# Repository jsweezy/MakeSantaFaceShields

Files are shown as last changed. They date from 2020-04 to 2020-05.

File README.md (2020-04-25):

# MakeSantaFaceShields
Face shield project for MakeSantaFe for COVID-19 aid for Santa Fe, NM.  

## Summary
Slight modification of the 3DVerkstan face shield frame to support stacking with PETG.

## Details
This was developed for stacking with PETG on a Prusa i3 Mk3. The original 3DVerkstan design is imported into 
OpenSCAD. A custom interface layer of 0.3mm is added between frames.  The interface layer consists of small 
cylinders along the arms of the frame.  Over the drip tray a bridge is added to support the next frame. The print 
settings for this layer are modified in Prusa Slicer. The nozzle temperature is lowered to 215C from the standard 250C, 
the fan is turned to 100%, and the print speed is slowed significantly.  This causes a delamination layer where the 
interface layer will fail to adhere to the frame below it. The interface layer will adhere to the frame above. 

There are two Perl scripts provided that generate custom GCODE and layer information for Prusa Slicer. These
are in the `Scripts` directory and include:\
`generate_gcode_for_PrusaSlicer.pl` - Generates custom GCODE\
`generate_layer_config_ranges_for_PrusaSlicer.pl` - Generates custom layer ranges

These scripts are used to modify Prusa project files, which are contained in a zip format.  If the print temperatures
need to modified then the Scripts need to be modified, the temperatures are set with a variable. The nozzle and bed temperatures need to also be set in Prusa Slicer. The procedure for modifying a project file is:

1) Make a directory for the project files and change to that director:\
`mkdir test_project`\
`cd test_project`
 
2) Unzip the Prusa project file.\
`unzip ../PrusaProjectFiles/8stack_test_petg.3mf`

3) Apply the custom GCODE generating script:\
`../Scripts/generate_gcode_for_PrusaSlicer.pl > Metadata/Prusa_Slicer_custom_gcode_per_print_z.xml`

4) Apply the layer config ranges script:\
`../Scripts/generate_layer_config_ranges_for_PrusaSlicer.pl > Metadata/Prusa_Slicer_layer_config_ranges.xml`

5) Recombine the files into a single Prusa project file:\
`zip ../PrusaProjectFiles/new_project.3mf -r *`

Now the new project file can be opened in Prusa Slicer and sliced. 

## Variations from the standard 3DVerkstan design

The goals was to make as few modifications to the 3DVerkstan design as possible. Such as maintaining the sweat drip tray. 
Some modifications for stacking fill in the drip tray. But the drip tray seems like an important design feature.  

### Drip Tray

The drip tray is slightly thickened to prevent damage when seperating the frames.  The original design was only 2 layers
thick for a 0.3mm layer height.  This also seemed to allow small holes if slight imperfections are made during a layer.  The
drip has been thickened to be 4 layers thick for strength and to prevent small holes. 

The interface layer contains a bridge below the drip tray.  The bridge will generally adhere well to the drip tray and provide another layer.  

### Arms

Small cylinders to seperate and support the frames have been added.  The design has been modified from IQLess (see reference below).  These cylinders can be easily removed but are not generally significant.   

### 

## References

### National Institues of Health page for this design:
https://3dprint.nih.gov/discover/3dpx-013306

### 3DVerkstan Page:
https://3dverkstan.se/protective-visor/

### Matterhackers Page for 3DVerkstan Design:
https://www.matterhackers.com/store/l/protective-face-shield/sk/M7LP9Q7M

### IQLess YouTube Channel
OpenSCAD support idea from: https://www.youtube.com/watch?v=apcrs6d_irc\
"Covid: Stacking Prusa RC3 and 3Dverkstan face shields Using Openscad"\
By iqless. OpenSCAD here is a modification of his file which can be found at:\
https://gist.github.com/patmandenver/847a0bf508b523487a3708c39c799950

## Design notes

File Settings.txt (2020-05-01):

Settings by material / manufacturer

* PETG

  - Overture
    * Diameter 1.27 
    * Bed Temp - 85/90 
    * Nozzle - 250C

  - Keene Village Plastics
    * Stacking has been well tested on Prusa Mk3
    * Diameter 1.25
    * Bed Temp - 85/90 -  May need to increase to prevent delamination during printing when fan to turned to 100%
    * Nozzle Standard - 250
    * Nozzle Interface - 215
    * Nozzle First Layer - 230
    * Fan Interface - 100%
    * Speed Interface - 3 mm/sec for perimeters, 6 mm/sec for infill

* PLA 

  - Overture
    * Diameter - 1.28 mm
    * Bed Temp - 60C
    * Nozzle Standard - 215C
    * Nozzle Interface - 180C
    * Nozzle First Layer - 195C
    * Notes:  Empty interface of 0.2 mm height with interface layer of 0.2 mm height

  - HatchBox
   
  - Matterhackers

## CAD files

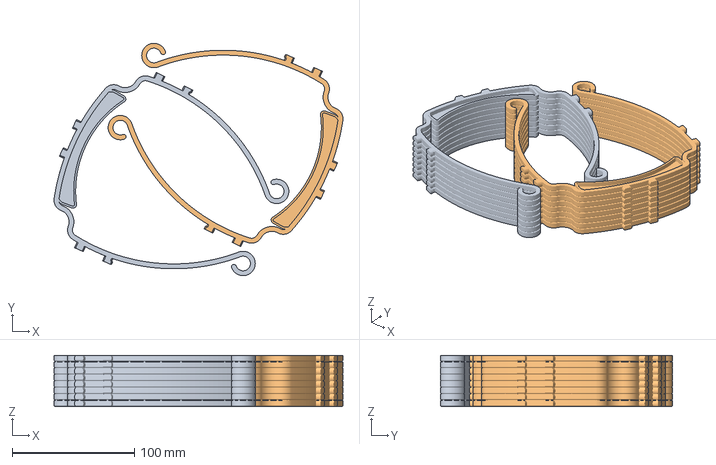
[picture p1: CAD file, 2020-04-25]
PrusaProjectFiles/PETG/2x8stack_petg.3mf
236.9 x 190.4 x 42.1 mm
3DVerkstan_6_hole_AMERICA_v3 x 20 (0.2mm gap) (1).STL x 2

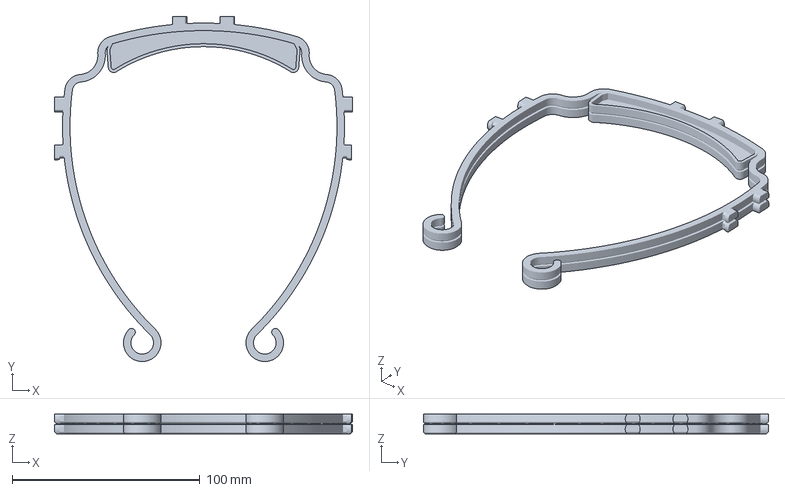
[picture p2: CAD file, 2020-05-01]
PrusaProjectFiles/PLA/2stack_pla_overture.3mf
158.5 x 183.6 x 10.4 mm

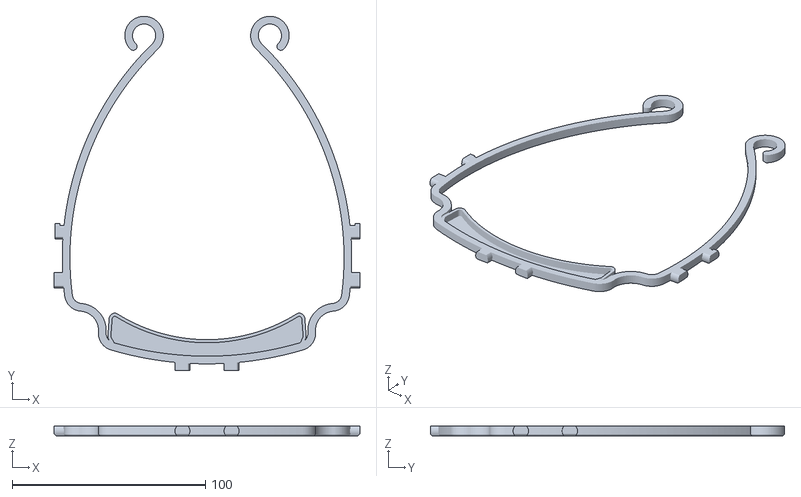
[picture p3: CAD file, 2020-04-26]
STLs/modified_frame.stl
158.5 x 183.6 x 5.00

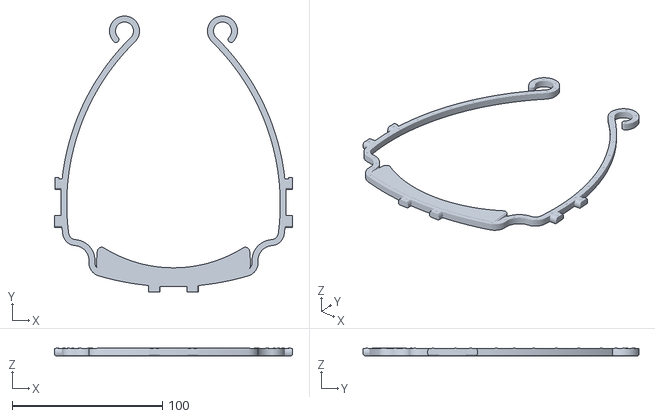
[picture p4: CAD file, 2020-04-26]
STLs/PETG/single_stackable_lower.stl
158.5 x 183.6 x 5.30

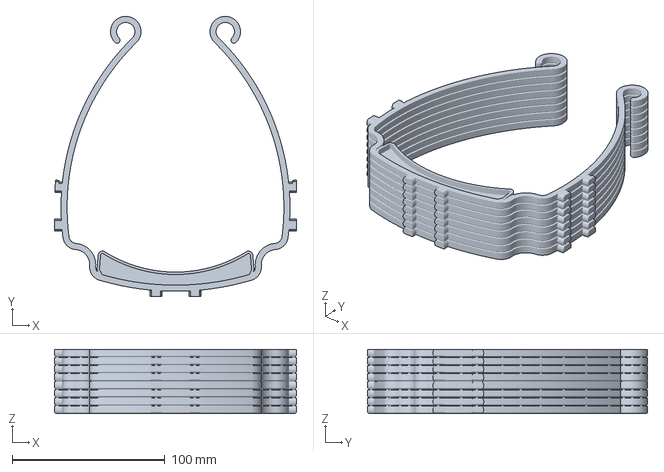
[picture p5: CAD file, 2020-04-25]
PrusaProjectFiles/PETG/8stack_test_petg.3mf
158.5 x 183.6 x 42.1 mm

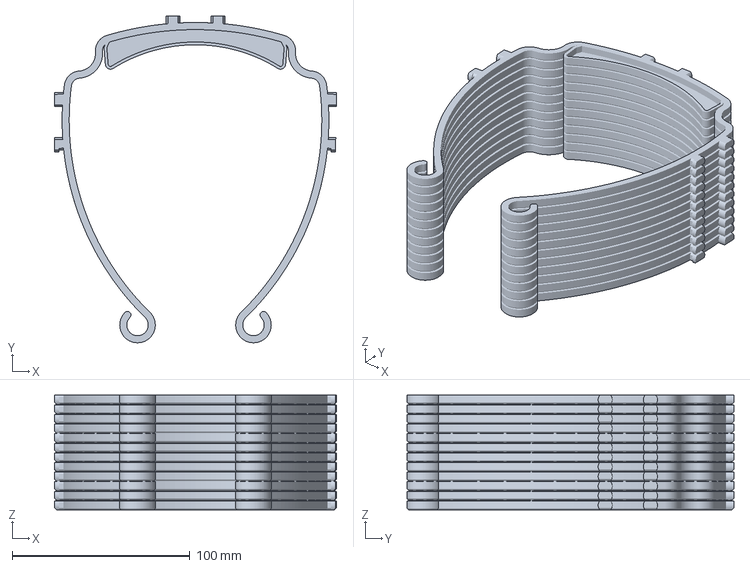
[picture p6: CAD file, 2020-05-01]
PrusaProjectFiles/PLA/12stack_pla_overture.3mf
158.5 x 183.6 x 64.4 mm

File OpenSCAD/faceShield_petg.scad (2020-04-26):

// File to stack 3DVerkstan Face Shield Frames
// OpenSCAD here is a modification of OpenSCAD file 
// which can be found at:
// https://gist.github.com/patmandenver/847a0bf508b523487a3708c39c799950

$fn=100;
num=5;
heigth=5;
floor_thickness=1.2;
bump=0.3;
cylinder_size=0.8;
extend_for_testing=0; //Set to 10 to see cylinders
test=1;  // 0 = no, 1 = yes

headband_file="../STLs/frame.stl";

main();

module main(){ 

rotate(180){
  
  if( num > 1 ) {  
  for(x=[0:num-2]){
    translate([0,0,x*(heigth+bump)]){
       import(headband_file, convexity=3); 
       color("blue") mirror_copy() floor(floor_thickness);
       //rotate(180) supports();
        color("blue") translate([0,0,heigth]) mirror_copy() bridge(bump);
       mirror_copy() cylinder_supports();
    }
  }
  }
  
  translate([0,0,(num-1)*(heigth+bump)]){
      import(headband_file, convexity=3); 
      color("blue") mirror_copy() floor(floor_thickness);
      if( test > 0 ) {
        //rotate(180) supports();
        translate([0,0,heigth]) mirror_copy() bridge(bump);
        mirror_copy() cylinder_supports();
      }
  }
  
}
}

module cylinder_supports() {
    //Supports on just one side
support_locs=[
             [12.5,31],
             //[12.5,17.3],
             //[48.3,4.6],
             [50,20.5],  
             [54.3,12],
             [56.5,6],
             [62,1.5],
             [69.5,-1],
             [77.5,-13],
             [73,-13],
             [73,-28],
             [77.0, -38.2],
             [72.5, -38.2],
             [70.0, -55],
             [67.0,-67],
             [56,-95],
             [62.7,-80],
             [47.2,-110],
             [26.3,-135],
             [29, -147.1],
             [37.8, -146],
             [38.3, -134.5],
             [25, -142.0],
             [40.25, -140.0],
             [35.8,-125]
             ];
             
  for(y = [0:len(support_locs)-1]){
    translate([0,0,floor_thickness])
    translate(support_locs[y]){
      color("#FF0000"){
        cylinder(heigth-floor_thickness+bump+extend_for_testing, 
                 cylinder_size, cylinder_size);
      }
    }
  }
}


//See https://en.wikibooks.org/wiki/OpenSCAD_User_Manual/Tips_and_Tricks#Create_a_mirrored_object_while_retaining_the_original
module mirror_copy(v = [1, 0, 0]) {
    children();
    mirror(v) children();
}

module floor(ft){
  color("#FF0000"){
    linear_extrude(ft){
        polygon([
                 
                 [0,29.1],
                 [10,28.8],
                 [15,28.4],
                 [20,28.0],
                 [25,27.3],
                 [30,26.6],
                 [35,25.6],
                 [40,24.5],
                 [45,23.2],
                 [48.1,22.4],
                 [48.1,20.1],
                 [49.0,19],
                 [50.5,16],
                 [49.8,6.5],
                 [49.5,5.5],
                 [49,5],
                 [48,4.55],
                 [47,4.7],
                 [46,5.3],
                 [44,6.5],
                 [43,7.1],
                 [39,9.2],
                 [35,11.05],
                 [32.5,12.07],
                 [30,13.0],
                 [25,14.7],
                 [20,16.0],
                 [15,17.0],
                 [10,17.7],
                 [5,18.15],
                 [0,18.3],
                ]
            );
    }
  }
}

module bridge(ft){
  overlap = 1.5;
  color("#FF0000"){
    linear_extrude(ft){
        polygon([
                 
                 [0,25.95+overlap],
                 [10,25.7+overlap],
                 [15,25.2+overlap],
                 [20,24.8+overlap],
                 [25,24.05+overlap],
                 [30,23.3+overlap],
                 [35,22.3+overlap],
                 [40,21.2+overlap],
                 [45,19.9+overlap],
                 [48.4,19.0+overlap],
                 [48.4,19.0+overlap],
                 [49.1+overlap,17.3+overlap],
                 [50.5,16],
                 [49.8,6.5],
                 [49.5,5.5],
                 [49,5],
                 [48,4.55],
                 [47,4.7],
                 [46,5.3],
                 [44,6.5],
                 [43,7.1],
                 [39,9.2],
                 [35,11.05],
                 [32.5,12.07],
                 [30,13.0],
                 [25,14.7],
                 [20,16.0],
                 [15,17.0],
                 [10,17.7],
                 [5,18.15],
                 [0,18.3],
                ]
            );
    }
  }
}

module supports() {
    support(43,-14.5,11.0,-26);
    support(50,-21.5,17.0);
    support(49.5,-22.0,17.0);
    support(44,-23.5,16.1); 
    support(36,-25.5,15.2); 
    support(27.5,-27,14.4); 
    support(19,-28.5,14.8);
    support(13,-32.5,19.8);
    support(-0,-29.5,16.2);
    support(-10,-29.5,20.0);
    support(-21.5,-28.0,21.5,40);
    support(-31,-26.5,28.0,40);
    support(-41,-24.5,17,35);
    support(-50,-18.0,13.5,-40);
    support(-49.25,-18.5,13.5,-40);
}

module support(x,y,l,r=45) {
    color("green"){
//        translate([x,y,floor_thickness]) rotate(r) 
//        cube([1,l,heigth-floor_thickness+bump+extend_for_testing]);
        translate([x,y,heigth]) rotate(r) 
        cube([1,l,bump+extend_for_testing]);
    }
}

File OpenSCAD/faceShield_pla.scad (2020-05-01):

// File to stack 3DVerkstan Face Shield Frames
// OpenSCAD here is a modification of OpenSCAD file 
// which can be found at:
// https://gist.github.com/patmandenver/847a0bf508b523487a3708c39c799950

$fn=100;
num=12;
heigth=5;
floor_thickness=1.2;
bump=0.2;
space=0.2;
cylinder_size=0.8;
extend_for_testing=0; //Set to 10 to see cylinders
test=0;  // 0 = no, 1 = yes
hide_bottom = 1; // 0 = no, 1=yes

headband_file="../STLs/frame.stl";

main();

module main(){ 

rotate(180){
  
  if( num > 1 ) {  
  for(x=[0:num-2]){
    translate([0,0,x*(heigth+bump+space)]){
       import(headband_file, convexity=3); 
       color("blue") mirror_copy() floor(floor_thickness);
       //rotate(180) supports();
        
       translate([0,0,space]) { 
       color("blue") translate([0,0,heigth]) mirror_copy() bridge(bump);
       mirror_copy() cylinder_supports();
       }
    }
  }
  }
  
  translate([0,0,(num-1)*(heigth+bump+space)]){
      import(headband_file, convexity=3); 
      color("blue") mirror_copy() floor(floor_thickness);
      if( test > 0 ) {
        translate([0,0,space]) {
        //rotate(180) supports();
        translate([0,0,heigth]) mirror_copy() bridge(bump);
        mirror_copy() cylinder_supports();
        }
      }
  }
  
}
}

module cylinder_supports() {
    //Supports on just one side
support_locs=[
             [12.5,31],
             //[12.5,17.3],
             //[48.3,4.6],
             [5,28.8],
             [25,26.9],  
             [40,24.0],  
             [51,20.5],  
             [54.3,12],
             [56.5,6],
             [62,1.5],
             [69.5,-1],
             [77.5,-13],
             [73,-13],
             [73,-28],
             [77.0, -38.2],
             [72.5, -38.2],
             [70.0, -55],
             [67.0,-67],
             [56,-95],
             [62.7,-80],
             [47.2,-110],
             [26.3,-135],
             [29, -147.1],
             [37.8, -146],
             [38.3, -134.5],
             [25, -142.0],
             [40.25, -140.0],
             [35.8,-125]
             ];
             
  for(y = [0:len(support_locs)-1]){
    translate([0,0,heigth])
    translate(support_locs[y]){
      color("#FF0000"){
        cylinder(bump+extend_for_testing, 
                 cylinder_size, cylinder_size);
      }
    }
  }
}


//See https://en.wikibooks.org/wiki/OpenSCAD_User_Manual/Tips_and_Tricks#Create_a_mirrored_object_while_retaining_the_original
module mirror_copy(v = [1, 0, 0]) {
    children();
    mirror(v) children();
}

module floor(ft){
  color("#FF0000"){
    linear_extrude(ft){
        polygon([
                 
                 [0,29.1],
                 [10,28.8],
                 [15,28.4],
                 [20,28.0],
                 [25,27.3],
                 [30,26.6],
                 [35,25.6],
                 [40,24.5],
                 [45,23.2],
                 [48.1,22.4],
                 [48.1,20.1],
                 [49.0,19],
                 [50.5,16],
                 [49.8,6.5],
                 [49.5,5.5],
                 [49,5],
                 [48,4.55],
                 [47,4.7],
                 [46,5.3],
                 [44,6.5],
                 [43,7.1],
                 [39,9.2],
                 [35,11.05],
                 [32.5,12.07],
                 [30,13.0],
                 [25,14.7],
                 [20,16.0],
                 [15,17.0],
                 [10,17.7],
                 [5,18.15],
                 [0,18.3],
                ]
            );
    }
  }
}

module bridge(ft){
  overlap = 1.5;
  color("#FF0000"){
    linear_extrude(ft){
        polygon([
                 
                 [0,25.95+overlap],
                 [10,25.7+overlap],
                 [15,25.2+overlap],
                 [20,24.8+overlap],
                 [25,24.05+overlap],
                 [30,23.3+overlap],
                 [35,22.3+overlap],
                 [40,21.2+overlap],
                 [45,19.9+overlap],
                 [48.4,19.0+overlap],
                 [48.4,19.0+overlap],
                 [49.1+overlap,17.3+overlap],
                 [50.5,16],
                 [49.8,6.5],
                 [49.5,5.5],
                 [49,5],
                 [48,4.55],
                 [47,4.7],
                 [46,5.3],
                 [44,6.5],
                 [43,7.1],
                 [39,9.2],
                 [35,11.05],
                 [32.5,12.07],
                 [30,13.0],
                 [25,14.7],
                 [20,16.0],
                 [15,17.0],
                 [10,17.7],
                 [5,18.15],
                 [0,18.3],
                ]
            );
    }
  }
}

module supports() {
    support(43,-14.5,11.0,-26);
    support(50,-21.5,17.0);
    support(49.5,-22.0,17.0);
    support(44,-23.5,16.1); 
    support(36,-25.5,15.2); 
    support(27.5,-27,14.4); 
    support(19,-28.5,14.8);
    support(13,-32.5,19.8);
    support(-0,-29.5,16.2);
    support(-10,-29.5,20.0);
    support(-21.5,-28.0,21.5,40);
    support(-31,-26.5,28.0,40);
    support(-41,-24.5,17,35);
    support(-50,-18.0,13.5,-40);
    support(-49.25,-18.5,13.5,-40);
}

module support(x,y,l,r=45) {
    color("green"){
//        translate([x,y,floor_thickness]) rotate(r) 
//        cube([1,l,heigth-floor_thickness+bump+extend_for_testing]);
        translate([x,y,heigth]) rotate(r) 
        cube([1,l,bump+extend_for_testing]);
    }
}

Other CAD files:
STLs/original_frame.stl

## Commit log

2020-04-25 Adding 2x8 stack and a settings text file
    [2x8stack_petg.3mf]
2020-04-26 Adding 5,12, and 20 stacks
    [faceShield.scad, single_stackable_lower.stl, single_stackable_upper.stl]
2020-05-01 Adding PLA versions
    [12stack_pla_overture.3mf, 2stack_pla_overture.3mf, 2x8stack_petg.3mf, 8stack_test_petg.3mf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]
